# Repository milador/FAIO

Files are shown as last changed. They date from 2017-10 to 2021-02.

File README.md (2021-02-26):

# FAIO - Feather All-in-One Switch Wings

FAIO assistive technology wings are assistive technology wings developed to provide a modular solution for those with high level of physical disabilities to interact with touch screen devices and personal computers.

## FAIO 1.0

Faio 1.0 is no longer under development and deprecated in favor of new FAIO 2.0 feather assistive technology wings.

## FAIO 2.0

Faio 2.0 is available in two different versions:

1. <a href="https://github.com/milador/FAIO-Multiplexer">FAIO-Multiplexer</a>
2. <a href="https://github.com/milador/FAIO-Sip-And-Puff">FAIO-Sip-And-Puff</a>

## License 

### MIT License

Copyright (c) 2017 Milador

Permission is hereby granted, free of charge, to any person obtaining a copy of this software and associated documentation files (the "Software"), to deal in the Software without restriction, including without limitation the rights to use, copy, modify, merge, publish, distribute, sublicense, and/or sell copies of the Software, and to permit persons to whom the Software is furnished to do so, subject to the following conditions:

The above copyright notice and this permission notice shall be included in all copies or substantial portions of the Software.

THE SOFTWARE IS PROVIDED "AS IS", WITHOUT WARRANTY OF ANY KIND, EXPRESS OR IMPLIED, INCLUDING BUT NOT LIMITED TO THE WARRANTIES OF MERCHANTABILITY, FITNESS FOR A PARTICULAR PURPOSE AND NONINFRINGEMENT. IN NO EVENT SHALL THE AUTHORS OR COPYRIGHT HOLDERS BE LIABLE FOR ANY CLAIM, DAMAGES OR OTHER LIABILITY, WHETHER IN AN ACTION OF CONTRACT, TORT OR OTHERWISE, ARISING FROM, OUT OF OR IN CONNECTION WITH THE SOFTWARE OR THE USE OR OTHER DEALINGS IN THE SOFTWARE.

<p align="center">
MIT License
</p>

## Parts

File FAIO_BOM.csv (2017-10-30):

Index | Version | Quantity | Part Number | Manufacturer Part Number | Description | Customer Reference | Backorder | Unit Price (CAD) | Total Price (CAD)
1 | All | 1 | 1597-1083-ND | 110990037 | GROVE 2MM 4PIN R/A CONN 10PACK |  | 0 | 2.05
2 | All | 1 | INA122PA-ND | INA122PA | IC OPAMP INSTR 120KHZ 8DIP |  | 0 | 8.63
3 | All | 1 | S5479-ND | PPPC041LGBN-RC | CONN FEMALE 4POS .100" R/A GOLD |  | 0 | 1.02
4 | All | 2 | CP-3536N-ND | MJ-3536N | CONN JACK MONO 3.5MM R/A |  | 0 | 0.94
5 | All | 1 | S7045-ND | PPPC121LFBN-RC | CONN HEADER FMALE 12POS .1" GOLD |  | 0 | 1.36
6 | All | 1 | S7049-ND | PPPC161LFBN-RC | CONN HEADER FMALE 16POS .1" GOLD |  | 0 | 1.7
7 | All | 1 | 2.4KQBK-ND | CFR-25JB-52-2K4 | RES 2.4K OHM 1/4W 5% AXIAL |  | 0 | 0.09
8 | All | 1 | 67-1327-ND | SSL-LX3059IGW | LED GRN/RED DIFF 3MM ROUND T/H |  | 0 | 0.8
9 | All | 2 | CF14JT300RCT-ND | CF14JT300R | RES 300 OHM 1/4W 5% AXIAL |  | 0 | 0.06
10 | All | 1 | BC1160CT-ND | K104Z15Y5VF5TL2 | CAP CER 0.1UF 50V Y5V RADIAL |  | 0 | 0.179
11 | All | 1 | 1528-1517-ND | 2829 | ADAFRUIT FEATHER 32U4 BLUEFRUIT |  | 0 | 40.2
12 | All | 1 | 1568-1493-ND | PRT-13851 | BATTERY LITHIUM 3.7V 400MAH |  | 0 | 6.17 | 64.199
13 | Sip-and-Puff | 1 | MPX12GP-ND | MPX12GP | SENSOR GAUGE PRESS 1.45PSI MAX |  | 0 | 14.33
14 | Sip-and-Puff | 2 | H762-ND | MHNZ 003 | HEX NUT 0.217" M3 |  | 0 | 0.0546
15 | Sip-and-Puff | 2 | RP809-ND | NMS-308 | MACHINE SCREW PAN PHILLIPS M3 |  | 0 | 0.49 | 79.6182
16 | Braille & Developer | 1 | 1597-1089-ND | 110990027 | GROVE 4PIN CABLES 5PACK 20CM |  | 0 | 3.97
17 | Braille | 6 | 679-2428-ND | MJTP1230 | SWITCH TACTILE SPST-NO 0.05A 12V |  | 0 | 0.16
 |  |  |  |  |  |  |  | Subtotal | 84.5482

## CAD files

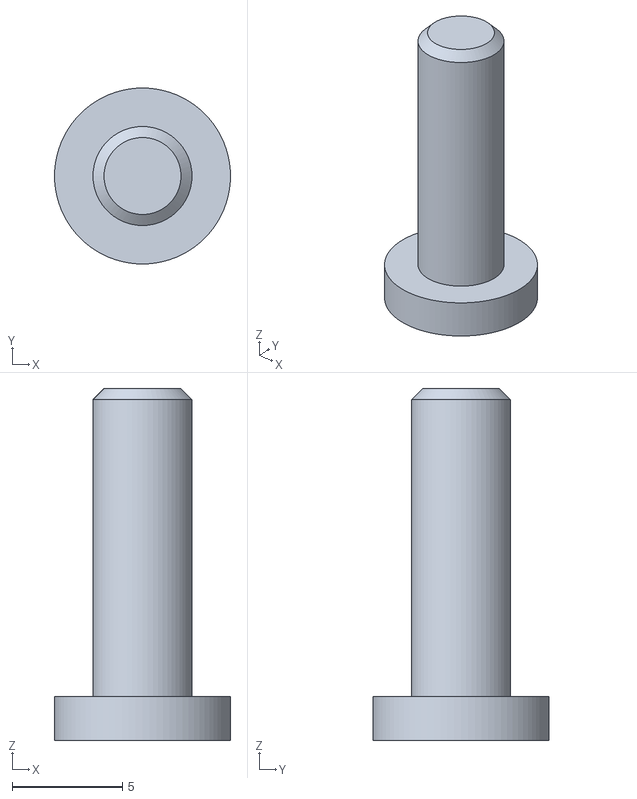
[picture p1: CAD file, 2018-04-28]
Hardware/Housing_design/FAIO Upper Case Button.stl
8.00 x 8.00 x 16.0

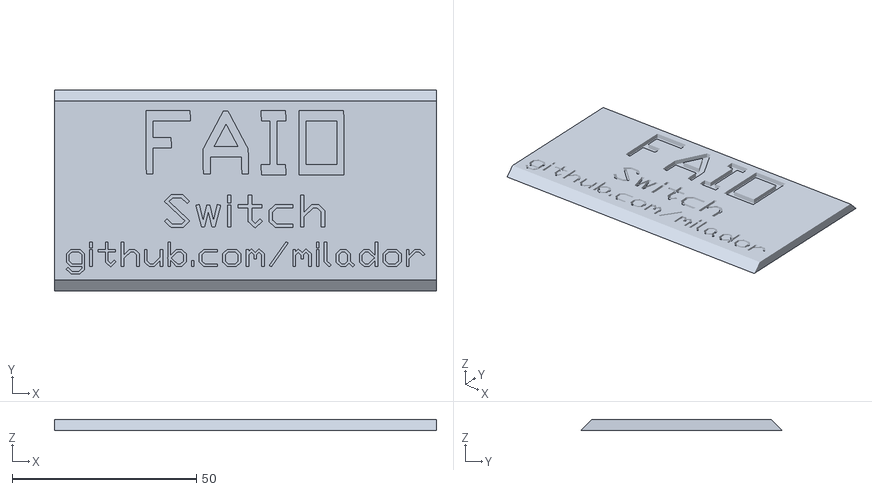
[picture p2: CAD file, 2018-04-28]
Hardware/Housing_design/FAIO Lower Cover.stl
103.6 x 54.6 x 3.00

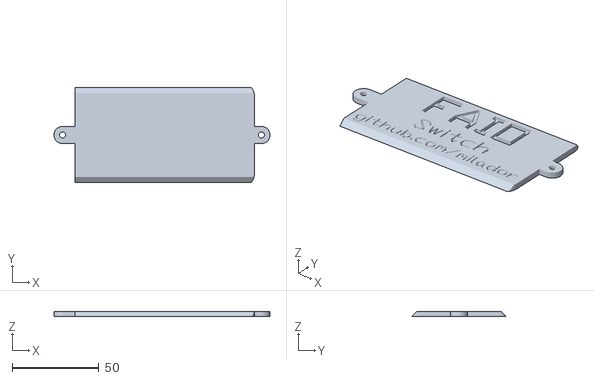
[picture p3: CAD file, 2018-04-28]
Hardware/Housing_design/FAIO Upper Cover.stl
124.6 x 54.6 x 3.00

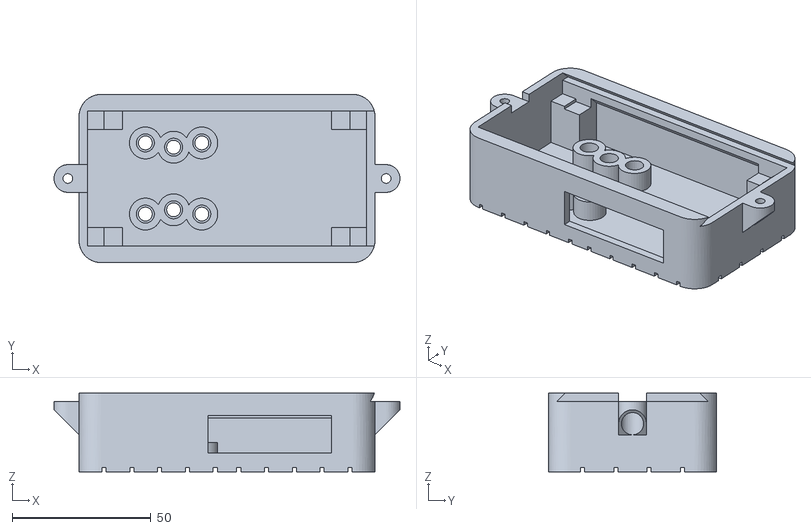
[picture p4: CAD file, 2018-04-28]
Hardware/Housing_design/FAIO Upper Case.stl
124.6 x 60.6 x 28.4

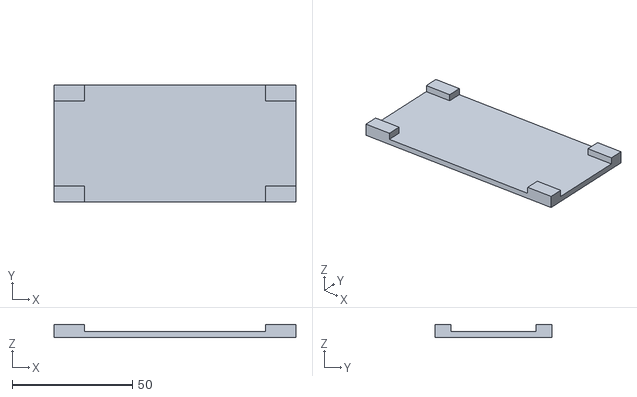
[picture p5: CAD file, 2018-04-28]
Hardware/Housing_design/FAIO Upper Sandwich.stl
100.6 x 48.6 x 5.50

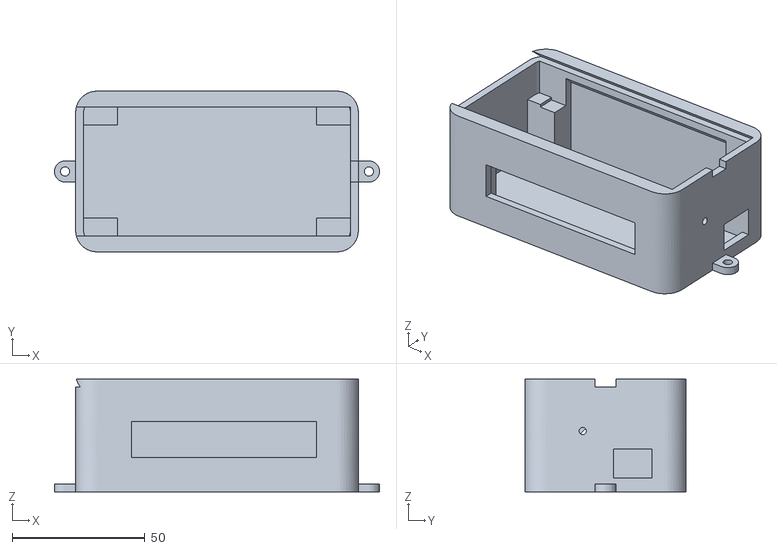
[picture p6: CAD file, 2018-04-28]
Hardware/Housing_design/FAIO Lower Case.stl
122.6 x 60.6 x 42.6

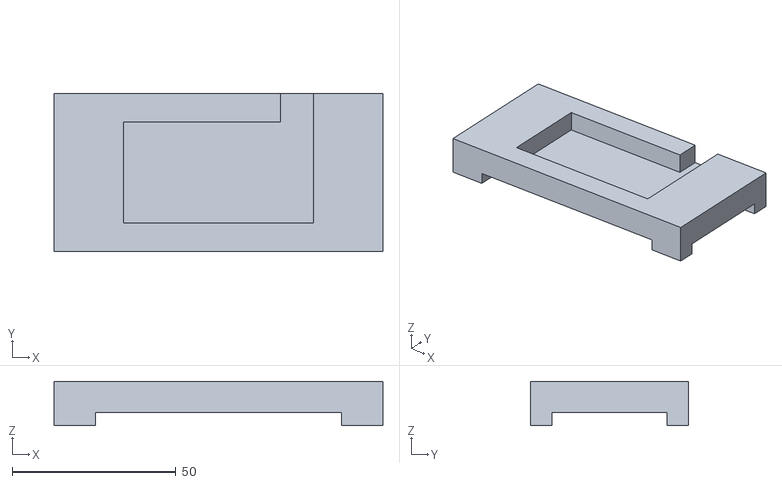
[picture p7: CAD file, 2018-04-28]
Hardware/Housing_design/FAIO Lower Sandwich.stl
100.6 x 48.2 x 13.5

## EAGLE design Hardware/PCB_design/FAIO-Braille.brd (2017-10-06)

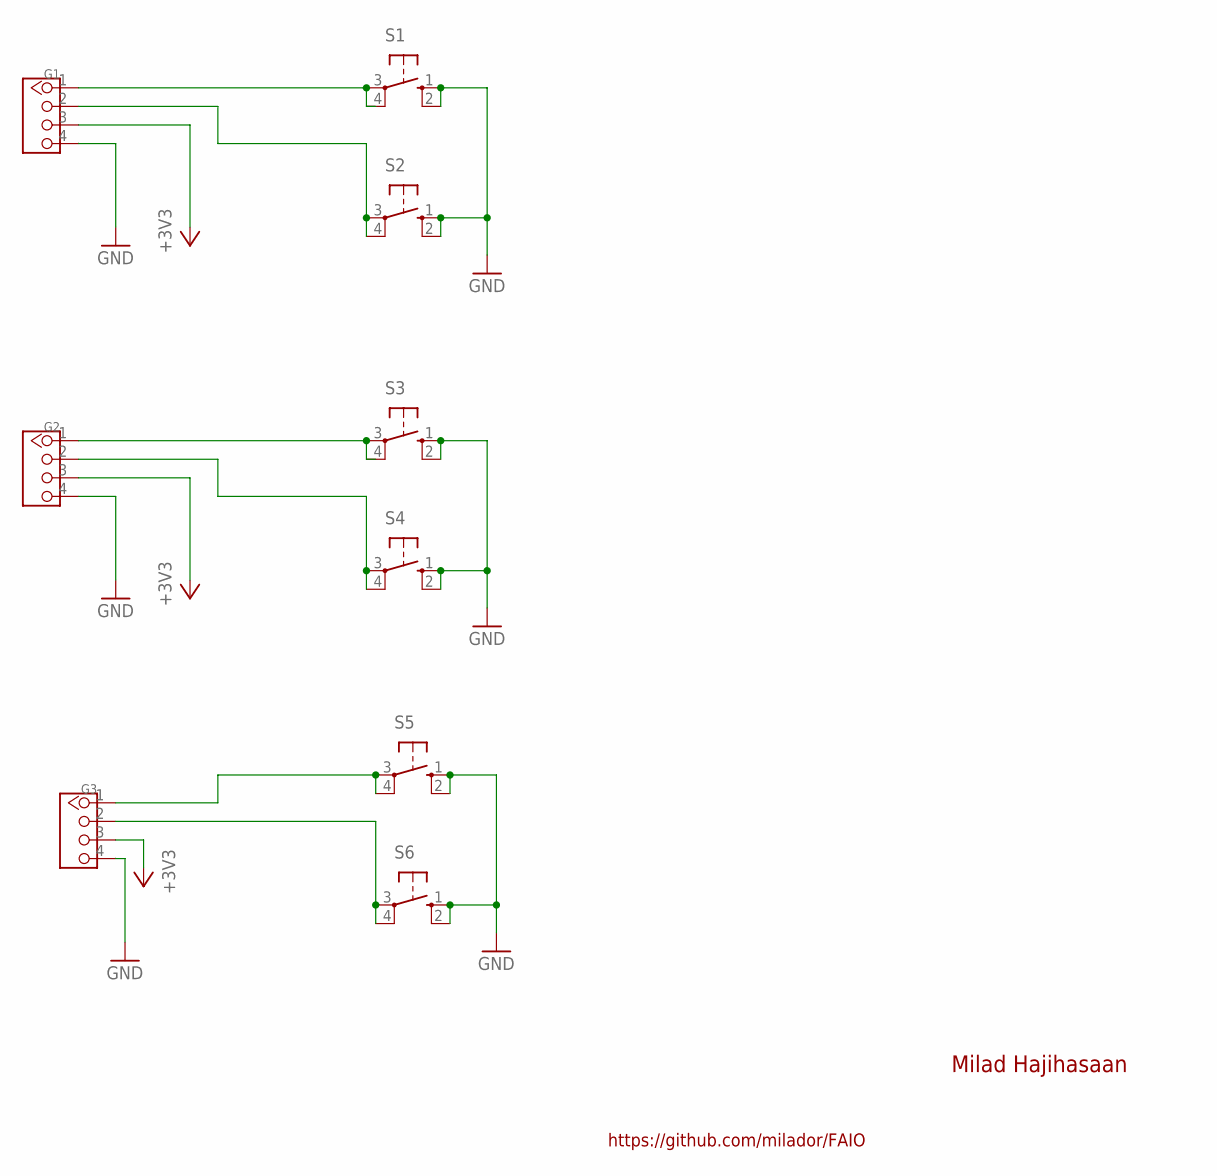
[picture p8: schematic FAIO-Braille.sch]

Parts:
G1, G2, G3: TWIG-4P-2.0'90D'; 4P-2.0-90D
S1, S2, S3, S4, S5, S6: 10-XX; B3F-10XX

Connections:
+3V3: G1.3, G2.3, G3.3
GND: G1.4, G2.4, G3.4, S1.1 (S), S1.2 (S1), S2.1 (S), S2.2 (S1), S3.1 (S), S3.2 (S1), S4.1 (S), S4.2 (S1), S5.1 (S), S5.2 (S1), S6.1 (S), S6.2 (S1)
unnamed: G1.1, S1.3, S1.4 (P1)
unnamed: G1.2, S2.3, S2.4 (P1)
unnamed: G2.1, S3.3, S3.4 (P1)
unnamed: G2.2, S4.3, S4.4 (P1)
unnamed: G3.2, S6.3, S6.4 (P1)
unnamed: G3.1, S5.3, S5.4 (P1)

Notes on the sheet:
Milad Hajihasaan
https://github.com/milador/FAIO

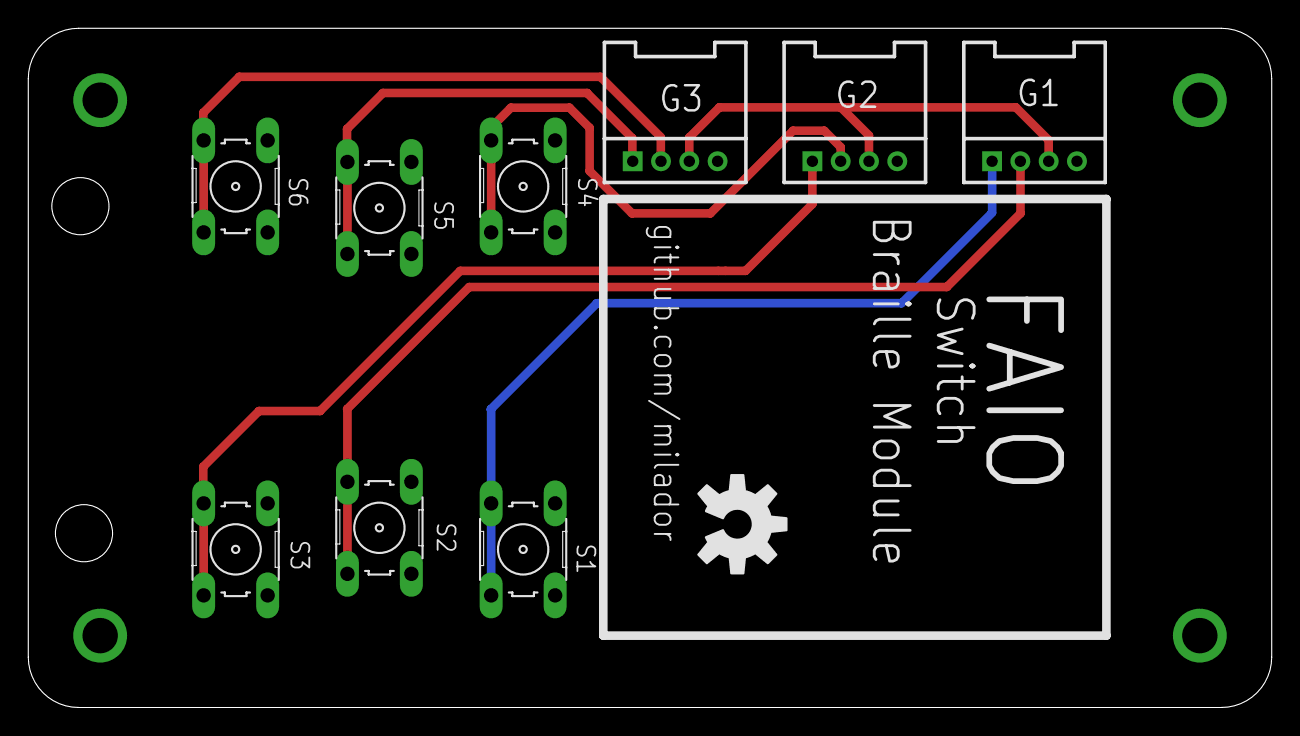
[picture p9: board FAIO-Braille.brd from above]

Board: 2 copper layers, 87.9 x 48.0 mm, 10 parts (0 on the bottom side), 8 nets.

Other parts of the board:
U$1: OSHW-LOGO-L

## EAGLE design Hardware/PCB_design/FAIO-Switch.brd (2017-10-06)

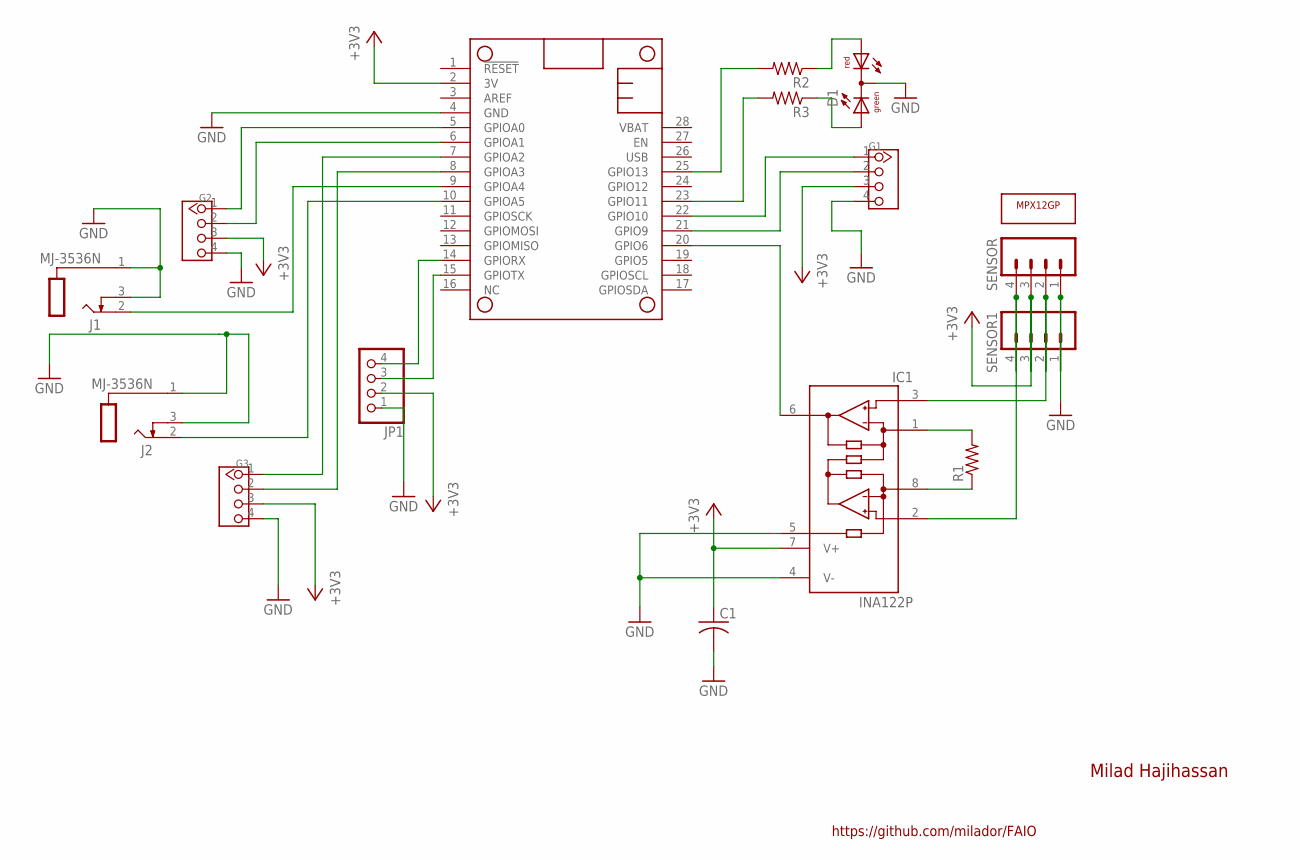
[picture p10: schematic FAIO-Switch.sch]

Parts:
C1: C-US025-024X044; C025-024X044
D1: DUOLED5MM
G1, G2, G3: TWIG-4P-2.0'90D'; 4P-2.0-90D
IC1: INA122P; DIL08
J1, J2: MJ-3536N
JP1: PINHD-1X4; 1X04
MS1: FEATHERWING_NODIM; FEATHERWING_DIM
R1, R2, R3: R-US_0204/7; 0204/7
SENSOR, SENSOR1: M04PTH; 1X04
U1: MPX12GP

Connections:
+3V3: C1.1, G1.3, G2.3, G3.3, IC1.7 (V+), JP1.2, MS1.2 (3V), SENSOR.3, SENSOR1.3
GND: C1.2, D1.K (C), G1.4, G2.4, G3.4, IC1.4 (V-), IC1.5 (REF), J1.1 (S), J1.3 (TS), J2.1 (S), J2.3 (TS), JP1.1, MS1.4 (GND), SENSOR.1, SENSOR1.1
unnamed: IC1.3 (+IN), SENSOR.2, SENSOR1.2
unnamed: IC1.2 (-IN), SENSOR.4, SENSOR1.4
unnamed: IC1.1 (RG), R1.2
unnamed: IC1.8 (RG), R1.1
unnamed: MS1.25 (GPIO13), R2.2
unnamed: D1.AR, R2.1
unnamed: D1.AG, R3.1
unnamed: MS1.23 (GPIO11), R3.2
unnamed: IC1.6 (OUT), MS1.20 (GPIO6)
unnamed: JP1.3, MS1.15 (GPIOTX)
unnamed: J1.2 (T), MS1.9 (GPIOA4)
unnamed: JP1.4, MS1.14 (GPIORX)
unnamed: G3.1, MS1.7 (GPIOA2)
unnamed: G1.1, MS1.22 (GPIO10)
unnamed: J2.2 (T), MS1.10 (GPIOA5)
unnamed: G2.2, MS1.6 (GPIOA1)
unnamed: G2.1, MS1.5 (GPIOA0)
unnamed: G1.2, MS1.21 (GPIO9)
unnamed: G3.2, MS1.8 (GPIOA3)

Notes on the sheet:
https://github.com/milador/FAIO
Milad Hajihassan

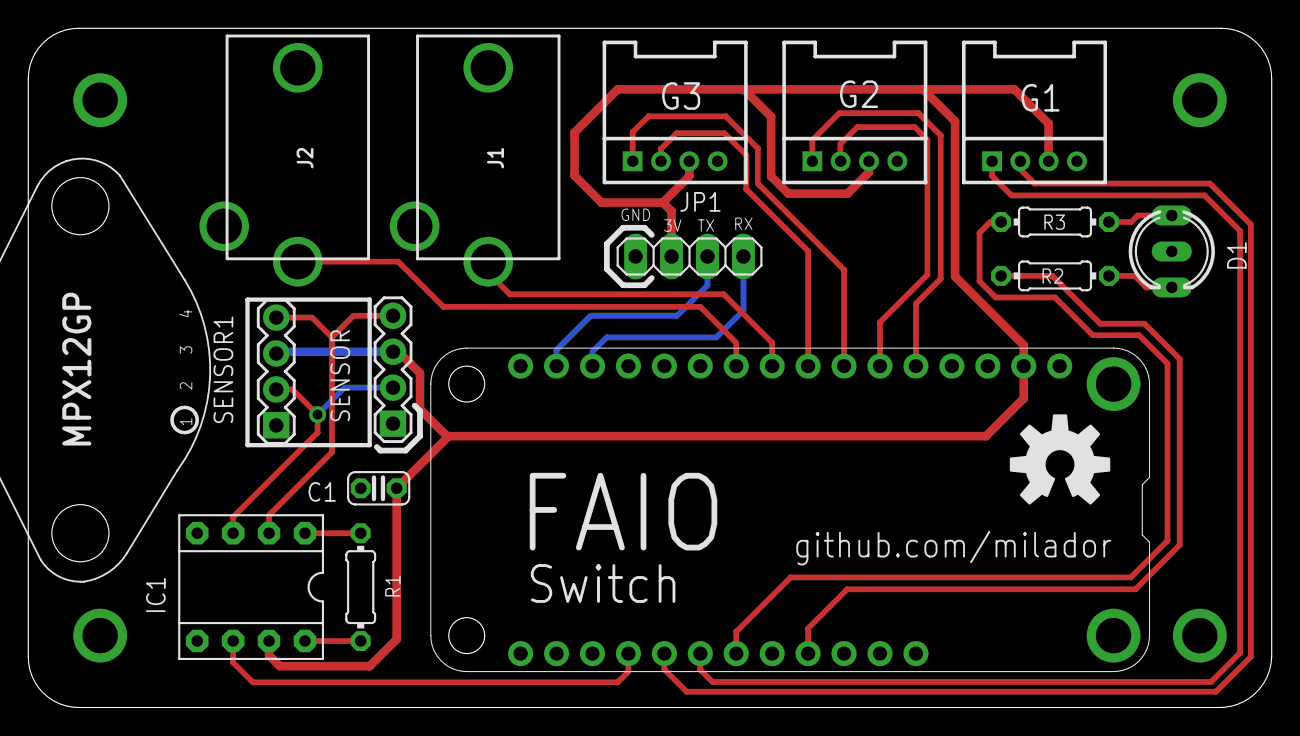
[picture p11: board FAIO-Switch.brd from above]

Board: 2 copper layers, 87.9 x 48.0 mm, 17 parts (0 on the bottom side), 21 nets.

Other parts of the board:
U$1: OSHW-LOGO-L

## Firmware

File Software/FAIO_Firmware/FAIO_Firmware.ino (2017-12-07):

//////////////////////////////////////
//
//FAIO ALL-IN-ONE switch
//
//Developed by Milad Hajihassan
//
//https://github.com/milador/FAIO
//
/////////////////////////////////////

#define MY_DEBUG 1
#define MY_TEST 1  //Testing mode = 0 , Production mode = 1
#define FACTORYRESET_ENABLE 0

#include "BluefruitRoutines.h"

//Input in Assignment
#define ADAPTIVE_SWITCH1_PIN A4
#define ADAPTIVE_SWITCH2_PIN A5
#define SIP_PUFF_SWITCH_PIN A7

#define BRAILLE_BUTTON11_PIN A1
#define BRAILLE_BUTTON12_PIN 10
#define BRAILLE_BUTTON21_PIN A2
#define BRAILLE_BUTTON22_PIN 9
#define BRAILLE_BUTTON31_PIN A3
#define BRAILLE_BUTTON32_PIN A0

#define LED1_PIN 11
#define LED2_PIN 13


// Variable Declaration 
int adaptiveSwitch1State;
int adaptiveSwitch2State;
float sipPuffPressureValue = 0.00;

float sipPressureThreshold;
float puffPressureThreshold;

int adaptiveSwitch1Enabled = 0;
int adaptiveSwitch2Enabled = 0;
int sipPuffPressureEnabled = 0;

//BRAILLE_BUTTON brailleButton
int brailleButton11State;
int brailleButton12State;
int brailleButton21State;
int brailleButton22State;
int brailleButton31State;
int brailleButton32State;

int braillePadEnabled = 0;
int brailleButton11Enabled = 0;
int brailleButton12Enabled = 0;
int brailleButton21Enabled = 0;
int brailleButton22Enabled = 0;
int brailleButton31Enabled = 0;
int brailleButton32Enabled = 0;

////////////////////////////
//Function to ranslate character to keyboard keycode and transmit
///////////////////////////

void pressKeyCode (uint8_t c) {
  ble.print(F("AT+BLEKEYBOARDCODE=00-00-"));
  uint8_t Code=c-'a'+4;
  if (Code<0x10)ble.print("0");
  ble.print(Code,HEX);
  ble.println(F("-00-00-00-00"));
  MESSAGE(F("Pressed."));
  delay(100);//de-bounce
  ble.println(F("AT+BLEKEYBOARDCODE=00-00"));
  MESSAGE(F("Released"));
}

////////////////////////////
//setup function
///////////////////////////

void setup() {
  //Initialize serial communications at 9600 bps
  Serial.begin(9600);
  pinMode(ADAPTIVE_SWITCH1_PIN, INPUT_PULLUP);
  pinMode(ADAPTIVE_SWITCH2_PIN, INPUT_PULLUP);
  pinMode(SIP_PUFF_SWITCH_PIN, INPUT);
  
  pinMode(BRAILLE_BUTTON11_PIN, INPUT_PULLUP);
  pinMode(BRAILLE_BUTTON12_PIN, INPUT_PULLUP);
  pinMode(BRAILLE_BUTTON21_PIN, INPUT_PULLUP);
  pinMode(BRAILLE_BUTTON22_PIN, INPUT_PULLUP);
  pinMode(BRAILLE_BUTTON31_PIN, INPUT_PULLUP);
  pinMode(BRAILLE_BUTTON32_PIN, INPUT_PULLUP);

  pinMode(LED1_PIN, OUTPUT);
  pinMode(LED2_PIN, OUTPUT); 
  
  initializeBluefruit();
  initialization();
}

////////////////////////////
//LED blink function
///////////////////////////

void ledBlink(int numberBlinks, int delayBlinks, int ledNumber ) {
      int ledBlinkNumber = ledNumber;
      for (int i = 0; i < numberBlinks; i++) {
        digitalWrite(ledBlinkNumber, HIGH);
        delay(delayBlinks);
        digitalWrite(ledBlinkNumber, LOW);
        delay(delayBlinks);
      }
}

////////////////////////////
//Initialization function
///////////////////////////

void initialization() {

   delay(500);
   
    //LED blinks to indicate start of initialization process
    ledBlink(2,100,LED1_PIN);
    ledBlink(2,100,LED2_PIN);

    //Initialization start message
    Serial.println("FAIO switch Initialization started.");
    Serial.println("----------");
    //adaptive switch initialization process to check if the switches are installed
    adaptiveSwitch1Enabled = digitalRead(ADAPTIVE_SWITCH1_PIN);
    if (adaptiveSwitch1Enabled == HIGH)
    {
      Serial.println("Adaptive Switch 1 is enabled.");
    }
    else
    {
      Serial.println("Adaptive Switch 1 is disabled.");
    }
    adaptiveSwitch2Enabled = digitalRead(ADAPTIVE_SWITCH2_PIN);
    if (adaptiveSwitch2Enabled == HIGH)
    {
      Serial.println("Adaptive Switch 2 is enabled.");
    }
    else
    {
      Serial.println("Adaptive Switch 2 is disabled.");
    }

    //Braille button initialization process to check if the Braille is installed
    brailleButton11Enabled = digitalRead(BRAILLE_BUTTON11_PIN);
    brailleButton12Enabled = digitalRead(BRAILLE_BUTTON12_PIN);
    brailleButton21Enabled = digitalRead(BRAILLE_BUTTON21_PIN);
    brailleButton22Enabled = digitalRead(BRAILLE_BUTTON22_PIN);
    brailleButton31Enabled = digitalRead(BRAILLE_BUTTON31_PIN);
    brailleButton32Enabled = digitalRead(BRAILLE_BUTTON32_PIN);
    if (brailleButton11Enabled && brailleButton12Enabled && brailleButton21Enabled && brailleButton22Enabled && brailleButton31Enabled && brailleButton32Enabled)
    {
      braillePadEnabled=1;
      Serial.println("Braille Pad is installed.");
    }
    else
    {
      braillePadEnabled=0;
      Serial.println("Braille Pad is not installed.");
    }
    
    //Pressure Sensor initialization process
    float normalPressureValue = (((float)analogRead(SIP_PUFF_SWITCH_PIN)) / 1023.0) * 3.30;
    //Check if Pressure Sensor is installed 
    if (normalPressureValue != 0.00)
    {
      //Find sip and puff pressure thresholds and show them 
      sipPuffPressureEnabled=1;
      sipPressureThreshold = normalPressureValue + 0.4; 
      puffPressureThreshold = normalPressureValue - 0.4; 
      Serial.print("Pressure Sensor Initialization completed. ");
      Serial.print("Sip Pressure Threshold is "); 
      Serial.print(sipPressureThreshold); 
      Serial.print(" And Puff Pressure Threshold is "); 
      Serial.println(puffPressureThreshold);    
    }
    else
    {
      sipPuffPressureEnabled=0;
      Serial.println("Pressure Sensor is not installed.");
    }
    
    //Initialization end message
    Serial.println("----------");
    Serial.println("FAIO switch initialization ended.");

    //LED blinks to indicate end of initialization process 
    ledBlink(2,100,LED1_PIN);
    ledBlink(2,100,LED2_PIN);
   
    delay(10000);
}

////////////////////////////
//Braille function
///////////////////////////

char braillePad(int pin11, int pin12, int pin21, int pin22, int pin31, int pin32) {
    char brailleChar;
    pin11=!pin11;
    pin12=!pin12;
    pin21=!pin21;
    pin22=!pin22;
    pin31=!pin31;
    pin32=!pin32;    
    if(pin11==1 && pin12==0 && pin21==0 && pin22==0 && pin31==0 && pin32==0) { brailleChar='a'; }
    else if(pin11==1 && pin12==0 && pin21==1 && pin22==0 && pin31==0 && pin32==0) { brailleChar='b'; }
    else if(pin11==1 && pin12==1 && pin21==0 && pin22==0 && pin31==0 && pin32==0) { brailleChar='c'; }
    else if(pin11==1 && pin12==1 && pin21==0 && pin22==1 && pin31==0 && pin32==0) { brailleChar='d'; }
    else if(pin11==1 && pin12==0 && pin21==0 && pin22==1 && pin31==0 && pin32==0) { brailleChar='e'; }
    else if(pin11==1 && pin12==1 && pin21==1 && pin22==0 && pin31==0 && pin32==0) { brailleChar='f'; }
    else if(pin11==1 && pin12==1 && pin21==1 && pin22==1 && pin31==0 && pin32==0) { brailleChar='g'; }
    else if(pin11==1 && pin12==0 && pin21==1 && pin22==1 && pin31==0 && pin32==0) { brailleChar='h'; }
    else if(pin11==0 && pin12==1 && pin21==1 && pin22==0 && pin31==0 && pin32==0) { brailleChar='i'; }
    else if(pin11==0 && pin12==1 && pin21==1 && pin22==1 && pin31==0 && pin32==0) { brailleChar='j'; }
    else if(pin11==1 && pin12==0 && pin21==0 && pin22==0 && pin31==1 && pin32==0) { brailleChar='k'; }
    else if(pin11==1 && pin12==0 && pin21==1 && pin22==0 && pin31==1 && pin32==0) { brailleChar='l'; }
    else if(pin11==1 && pin12==1 && pin21==0 && pin22==0 && pin31==1 && pin32==0) { brailleChar='m'; }
    else if(pin11==1 && pin12==1 && pin21==0 && pin22==1 && pin31==1 && pin32==0) { brailleChar='n'; }
    else if(pin11==1 && pin12==0 && pin21==0 && pin22==1 && pin31==1 && pin32==0) { brailleChar='o'; }
    else if(pin11==1 && pin12==1 && pin21==1 && pin22==0 && pin31==1 && pin32==0) { brailleChar='p'; }
    else if(pin11==1 && pin12==1 && pin21==1 && pin22==1 && pin31==1 && pin32==0) { brailleChar='q'; }
    else if(pin11==1 && pin12==0 && pin21==1 && pin22==1 && pin31==1 && pin32==0) { brailleChar='r'; }
    else if(pin11==0 && pin12==1 && pin21==1 && pin22==0 && pin31==1 && pin32==0) { brailleChar='s'; }     
    else if(pin11==0 && pin12==1 && pin21==1 && pin22==1 && pin31==1 && pin32==0) { brailleChar='t'; }
    else if(pin11==1 && pin12==0 && pin21==0 && pin22==0 && pin31==1 && pin32==1) { brailleChar='u'; }
    else if(pin11==1 && pin12==0 && pin21==1 && pin22==0 && pin31==1 && pin32==1) { brailleChar='v'; }
    else if(pin11==0 && pin12==1 && pin21==1 && pin22==1 && pin31==0 && pin32==1) { brailleChar='w'; }
    else if(pin11==1 && pin12==1 && pin21==0 && pin22==0 && pin31==1 && pin32==1) { brailleChar='x'; }
    else if(pin11==1 && pin12==1 && pin21==0 && pin22==1 && pin31==1 && pin32==1) { brailleChar='y'; }
    else if(pin11==1 && pin12==0 && pin21==0 && pin22==1 && pin31==1 && pin32==1) { brailleChar='z'; }
    else if(pin11==0 && pin12==1 && pin21==0 && pin22==1 && pin31==1 && pin32==1) { brailleChar='#'; }
               
    return brailleChar;
}

////////////////////////////
//Main loop function
///////////////////////////
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

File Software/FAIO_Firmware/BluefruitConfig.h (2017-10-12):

// COMMON SETTINGS
// ----------------------------------------------------------------------------------------------
// These settings are used in both SW UART, HW UART and SPI mode
// ----------------------------------------------------------------------------------------------
#define BUFSIZE                        128   // Size of the read buffer for incoming data
#define VERBOSE_MODE                   true  // If set to 'true' enables debug output


// SOFTWARE UART SETTINGS
// ----------------------------------------------------------------------------------------------
// The following macros declare the pins that will be used for 'SW' serial.
// You should use this option if you are connecting the UART Friend to an UNO
// ----------------------------------------------------------------------------------------------
#define BLUEFRUIT_SWUART_RXD_PIN       9    // Required for software serial!
#define BLUEFRUIT_SWUART_TXD_PIN       10   // Required for software serial!
#define BLUEFRUIT_UART_CTS_PIN         11   // Required for software serial!
#define BLUEFRUIT_UART_RTS_PIN         -1   // Optional, set to -1 if unused


// HARDWARE UART SETTINGS
// ----------------------------------------------------------------------------------------------
// The following macros declare the HW serial port you are using. Uncomment
// this line if you are connecting the BLE to Leonardo/Micro or Flora
// ----------------------------------------------------------------------------------------------
#ifdef Serial1    // this makes it not complain on compilation if there's no Serial1
  #define BLUEFRUIT_HWSERIAL_NAME      Serial1
#endif


// SHARED UART SETTINGS
// ----------------------------------------------------------------------------------------------
// The following sets the optional Mode pin, its recommended but not required
// ----------------------------------------------------------------------------------------------
#define BLUEFRUIT_UART_MODE_PIN        12    // Set to -1 if unused


// HARDWARE SPI SETTINGS
// ----------------------------------------------------------------------------------------------
// The following macros declare the pins to use for HW SPI communication.
// SCK, MISO and MOSI should be connected to the HW SPI pins on the Uno, etc.
// This should be used with nRF51822 based Bluefruit LE modules that use SPI.
// ----------------------------------------------------------------------------------------------
#define BLUEFRUIT_SPI_CS               8
#define BLUEFRUIT_SPI_IRQ              7
#define BLUEFRUIT_SPI_RST              4    // Optional but recommended, set to -1 if unused

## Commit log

2017-08-31 Added the part list
    [FAIO_BOM.xlsx]
2017-09-30 Updated Components list
    [FAIO_BOM.xlsx]
2017-09-30 Added PCB files
    [FAIO-Braille.brd, FAIO-Braille.sch, FAIO-Switch.brd, FAIO-Switch.sch]
2017-09-30 Added Lithium Ion Polymer Battery to components list
    [FAIO_BOM.xlsx]
2017-10-06 Updated BOM and board layouts
    [FAIO-Braille.brd, FAIO-Switch.brd, FAIO_BOM.csv, FAIO_BOM.xlsx]
2017-10-08 Updated Part list
    [FAIO_BOM.csv, FAIO_BOM.xlsx]
2018-04-28 Added housing STL Files
    [FAIO Lower Case.stl, FAIO Lower Cover.stl, FAIO Lower Sandwich.stl, FAIO Upper Case Button.stl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]

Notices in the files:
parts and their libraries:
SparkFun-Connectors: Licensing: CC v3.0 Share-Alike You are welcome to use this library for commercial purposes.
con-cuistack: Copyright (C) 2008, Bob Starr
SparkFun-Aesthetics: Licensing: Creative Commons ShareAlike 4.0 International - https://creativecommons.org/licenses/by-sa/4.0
